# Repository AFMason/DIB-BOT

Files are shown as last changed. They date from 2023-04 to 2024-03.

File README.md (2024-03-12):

# DIB-BOT
Your guide to building and using DIB-BOT. This guide assumes you do not have a 3D printer already, and you've bought a new Ender3 for this project. If you've already got a 3D printer you can obviously skip some of these steps, or you might need to adapt. Good luck!
![Uploading 20230316_173502.jpg…]()

## Initial Setup
Step 1:
Acquire all the materials listed in "Shopping list.md"

Step 2:
Assemble the Ender 3. I found the method described by Chuck Hellebuyck (CHEPclub - Home, https://youtu.be/2Th2e7wTNV0) to be really useful. This differs slightly from the manufacturers instructions, and results in a more well-aligned printing bed. Of particular importance is to really tighten the belts - this improves the spatial resoltion of the printer and will help reduce positional variation of droplets between different wells.

Step 3: 
Do some test prints with the Ender3 to check if it has been assembled properly. You may need to tighten/align/troubleshoot before the Ender3 behaves reliably. For example the benchy boat, or CHEPs concentric circles.

Step 4: 
Print the nanoject holder (Nanoject_holder.stl, Nanoject_holder.gcode). I used PETG, you might be able to use another filament, if you don't use PETG you'll want to re-slice the .stl file as Nanoject_holder.gcode has been optimised for PETG. After printing, the bridge support and any small printing errors were carefully removed from the Nanoject holder with a scalpel and 120 grit sandpaper.

For DIB-BOT V1, you can stop here and start playing around with it. However, if you want to further automate the droplet deposition process and have the Ender3 control the Nanoject, you need to complete the following steps.

## Running DIB-BOT

### Developing a custom gcode print method

For this project I had to learn how to write gcode. This coding language has its roots in the first CNC metalworking machines from the 1950s, and is one of the first "high-level" programming languages. As such, its relatively simple to learn, particularly for the rudimentary cartesian movements that are performed by DIB-BOT. There are plenty of resources on Youtube, but I found websites like https://marlinfw.org/meta/gcode/ particularly useful for understanding specific commands (and Marlin is the "flavour" of gcode that the Ender3 runs on).  

I've annotated all of my code uploaded to this github, but below I've listed some of the most important commands:
```
G90 ;enable absolute positioning, so all movement commands are calculated relative to (0,0,0)
G91 ;enable relative positioning, so all movement commands are calculated relative to the current position
G28 ;Home all axes - this needs to happen at the start of every method to "zero" the axes

G1 X1 Y2 Z3 F3000 ; G1 is the basic move command. This particular line tells the printer to move to (1,2,3) in absolute positioning or move (+1,+2,+3) in relative positioning, at a speed of 3000 mm/min.
G4 S5 ;Pause for 5 seconds

M0 ;pause the print/method. The operator will need to press the resume button on the printer to continue the method. Useful for inserting indefinite pauses.
M0 Hello World ;Pauses the method and displays a little message, "Hello World" in this example. Useful for reminding the operator of what to do at every point, such as change the sample or check the tip calibration.

M104 S0 ;sets the hot end to 0 °C, to ensure nothing gets hot
M190 S0 ;sets the bed temperature to 0 °C
M107 ;turns the fan (FAN3) on the hot end OFF
M106 ;turns FAN3 ON
M300 P100 ;tells the 3D printer to emit a short beep from its internal speaker, length 100 ms in this example
```

**How to write/review/edit gcode**

You can use any plain text editor like Notepad. Just make sure you save it as a *.gcode file (for example, a file named "test print.gcode"), otherwise the Ender3 won't be able to read it.

I edit my gcode in Notepad++ (https://notepad-plus-plus.org/downloads/) using the custom language profile created by Eldar Gerfanov (https://zero-divide.net/?article_id=4809_notepad-absolutely-free-g-code-editor-with-code-highlighting) which just makes writing code a little bit cleaner and easier in my experience. If you're going to write a lot of gcode you'll be doing lots of find and replace actions which works well in Notepad ++.

### Importance of calibration

The 3D printer doesn't know where your 384-well plate is, how deep the wells are, or how long the pulled microcapillary is. At the start of all my gcode methods you'll find some calibration code:
```
G28 ; Home all axis
G1 Z150 F3000 ; Lift Z axis and load first solution
M106; fan on to open relay, enable fill/empty/inject button
M0 load dye; pause print, load first droplet solution
G1 X45.0 Y129.9 F3000
G1 Z68.3 
M0 check nozzle height
G1 Z70
G1 X51.1 Y162.4 F3000; Move to start - 1A - check position of plate
G4 S1
M300 P100 ; short beep
G4 S1
M300 P100
G4 S1
M300 P100
M0 check start position; Pause print, check plate alignment
```
The first G1 move lifts the print head to +150 mm, and then pauses. This is to provide plenty of clearance from the well plate, so the tip doesn't crash into it, and raises it to a nice ergonomic position to load the first aqueous solution. It then navigates to X45, Y129.9, Z68.3 before pausing again. Z68.3 was the exact position that was selected where the top of the well plate just touched the tip of the pulled capillary. It is important to mount the nanoinjector deliberately high in the harness, such that when you're at Z68.3, you need to lower the nanoinjector down a few millimeters manually to find the perfect "just touching" position. ***If you don't do this step you run the risk of crashing your tip into the plate during this first calibration step.*** 

Next, the print head will raise up to Z70 - 1.7 mm above the plate surface. This is the height that throughout the method is used to travel in x and y. It will then navigate to X51.1 Y162.4 and the pause again for you to check the xy calibration. If you're using the 3D printed well plate holder I have designed, and aligned it the left and bottom edges of the build plate, then the nozzle should be centered over well 1A. If its not centered, you have 2 options - move the well plate, or change the code. I do the latter, and use the manual movement controls on the printer itself to find the position of 1A, and then update the calibration code. ***This is vital to get correct, as the majority of the patterning gcode is executed in relative positioning (G91). So, if you don't nail the position of the first well, every other well won't work either***

### Materials

**1. Pulling capillaries to make nanoinjector nozzles** Micropipettes were pulled using a Sutter P-87 capillary puller. The puller was set in the following manner: heat = ramp (672), pull = 0, v = 40, time = 250, pressure = 500. The puller should loop twice, with the capillary breaking on the second loop. If the capillary snaps on the first loop, lower the heat and/or velocity parameters in small increments. Before mounting in the Nanoject, micropipettes were confidently but gently stabbed through a single sheet of kimwipe paper to break the tip cleanly, which was verified using a transmitted light microscope (4x objective). You can find a great resource for variations to this method in the "methods" folder, "capillary cookbook.pdf".

You can pull capillaries manually (as in heat up a capillary over a bunsen burner and pull) but this results in pretty rough nozzles. These instruments are regularly used in electrophysiology labs - if you're at a university, ask around. I didn't have one in my lab, but would pull batches of capillaries that last for a month or two. I have not yet found a good low-cost/open source capillary puller...

**2. Preparing lipid solutions** The "lipid-out" approach was employed, where lipids are dissolved in the oil phase. DPhPC was purchased from Sigma-Aldrich as a powder. The entire 200 mg vial was dissolved in chloroform to a concentration of 100 mg/ml. Aliquots of this stock solution were transferred to 2 mL glass HPLC vials and dried to a film under a stream of nitrogen. For example, 50 uL aliquots results in 10 mg per vial, perfect for redissolving with 1 mL of hexadecane to get 5 mg/mL. DPhPC films were further dried in vacuo for at least 18 hours before further use, and stored under nitrogen at -20 °C if not used immediately. 

**3. Preparing aqueous solutions** Full details can be found in the preprint, this depends on the experiment. Typically, aqueous solutions were buffered with 10 mM HEPES at pH 7, with approximately 1 M KCl.

### Running a custom gcode print method

**1. Load a pulled capillary** Remove the black plastic collet from the NanojectII and carefully remove the upper-most black O-ring from the stainless steel piston. You can do the following back-filling of the capillary in many different ways, but this worked best for me. The main thing is you want to fill the capillary with your oil phase without breaking the sharp end, and without introducing any air bubbles. First, I filled a 1 mL plastic syringe with hexadecane, and attached a blunt stainless steel 30g x 2" needle, gently depressing the plunger of the syringe to expel any air from the needle. Second, I placed the collect on the capillary before I pushed the black O-ring onto the blunt end of the pulled capillary and adjusted it to be 1-2 mm from the end (as this is where it will sit when it is inserted again in the Nanoject). I then back filled the pulled capillary, leaving a small amount to flow over the top of the blunt end. Using a kimwipe, I then gently blotted away any excess oil on the outside of the capillary and O-ring, but leaving the blunt aperture of the capillary with excess oil. Next, I carefully installed the capillary back onto the Nanoject, not tightening the collet too much. If there is any air in the capillary next to the stainless steel piston, do it again. Air bubbles are compressible and this can introduce issues with injection volume consistency, or failed injections (ie you press Inject and nothing comes out).

Once the capillary is back-filled with hexadecane, press "Empty" on the Nanoject control until the air is expelled from the sharp end. Mount the Nanoject in the 3D-printed harness on the x-stage of the Ender3, *taking care to mount the Nanoject high, so that when the next calibration step is carried out, you need to lower it. If you don't have it high enough, it may crash during the initialisation, breaking your tip. Pulled capillaries vary in length so this is impossible to fix for now. Finally, unless you have upgraded to v3 with automated sample loading, you can load your aqueous sample.
[insert image of correct loading height]

**2. Perform the calibration steps as outlined above**

**3. Droplet injection** With v1 of the DIB-BOT, there is no communication between the 3D printer and the Nanoject. In v1 methods, a pause is programmed when the nozzle is at the bottom of each well. The Ender3 will beep at you when its ready and thats your cue to press the "Inject" button on the Nanoject control box, and then push the knob in on the Ender3 to continue the method. I got pretty bored of this very quickly and modified the DIB-BOT to streamline this process, but it does work.

**4. Exchanging nozzle contents** If you want to have different aqueous contents on either side of the bilayer, you'll need to change the contents of your nozzle. In V1 methods, the following code facilitates this (was written for a 96 well plate with 9 mm centre-to-centre distance):
```
;change pipette contents
G1 Z80 ;lift pipette high
G1 Y-170 F3000 ;pushes plate back and out of the way
G4 S1
M25; pause to rinse +reload pipette
G1 Y161 F3000 ; brings plate
G1 Z-68; lower to travel position
M300 P100 ; short beep
G4 S2
M25 ; Pause print
```
After the nozzle has been raised up, carefully "Empty" the Nanoject, and then "Fill" with buffer or Milliq. Repeat this 2-3 times before filling with the next sample. It's tricky (which inspired v3 development) and you want to avoid touching the tip of the nozzle against the wall of the eppendorf tube, as this can cause imperceptible movement to the capillary and result in droplets not landing adjacent to the first droplet (thus failing to make a DIB). All the results from the paper were generated using v4 methods but you can still definitely make lots of good DIBs if you've got a steady hand with v1/v2.

## DIB-BOT v2: Automated droplet injection

Now you're ready to upgrade to v2 of DIB-BOT. This involves some hardware tinkering that may void your warranty on the Ender3 (as it involves opening up the motherboard case), and some additional elements in the gcode. The effort is worth it though, the result is a lot less button pushing.

### Modifications to DIB-BOT

1. You need to make a wire that connects the NanojectII to the Ender3. One end of this is a standard 3.5 mm 2-pole connector (same as you would find on  wired headphones). You can find this part easily online or at your local hobby/electronics store (I bought one from Jaycar here in Australia for less than $1). You'll need to solder the ends of the wire to the terminals inthe 3.5 mm connector, I don't think the polarity matters as the action of closing the circuit triggers the NanojectII, but you can follow my example which definitely works.
Artboard 1-100

2. The other end of this cable will connect to the [CON2] screw connectors on the relay module (also from Jaycar, Cat# XC4419, 5V relay, $7.95). As per the above circuit diagram, connect one wire to the "common" screw, and the other to the "NO" screw (stands for normally open, ie the resting state is an open circuit).


3. Then connect using female-female jumper leads the relay to the Ender3 motherboard, as per the circuit diagram above and photo below.


Orange wire from "S" (signal) on relay connects to negative terminal of FAN1
Red wire from "V" (supply voltage) on relay connects to Pin 2, denoted V, on the BLTouch header
Black wire from "G" (ground) on relay connects to Pin 1, denoted G, on the BLTouch header

### Modifications to gcode

-fan off/fan on cycling

-importance of delays

### Running DIB-BOTv2

## DIB-BOTv3: Semi-automated sample loading

The trickiest part of running DIB-BOTv2 is now sample exchange and rinsing the capillary - it is very easy to either break the tip of the capillary or nudge it so that its x/y position is out by 10s of microns, potentially decreasing your DIB yield. With DIB-BOTv3, the operator no longer has to hold a small tube up to the capillary; instead the capillary translates to one of 3 eppendorf tube holders in the plate holder to either dump to waste, fill with clean buffer/water, or load new sample.

### Modifications to gcode

### Running DIB-BOTv3

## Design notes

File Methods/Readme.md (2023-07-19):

In this folder you'll find a selection of the most recent gcode method files I have written. They have been written for a specific experiment which is described in detail in the soon to be released manuscript. In the sub-folder "Historical methods" you can find earlier, less refined methods, to document the progression of the DIB-BOT.

In each gcode files I have annotated each line that matters, to explain what that line of code does to the printer. This should hopefully allow you to make adjustments easily.

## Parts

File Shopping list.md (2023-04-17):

Everything you need to build the DIB-BOT. For materials needed to conduct experiments, check out the paper.
 
1. PETG filament (https://www.inkstation.com.au/2102/petg-3d-filament-175mm-silver-1kg-roll-p-18777.html?queryID=29b280d231a7040a4940cce4f01be405&objectID=18591#18591)
2. Dongle single channel 5 V relay (https://www.jaycar.com.au/duinotech-arduino-compatible-5v-relay/p/XC4419?pos=1&queryId=fd5d4861d8dd5a5220dddf146e065b07&sort=relevance&searchText=relay%20arduino) 
3. Jumper cables (https://www.jaycar.com.au/jumper-lead-mixed-pack-100-pieces/p/WC6027?pos=2&queryId=66a482975f8ff08bda1e47b8542ebf3a)
4. 3.5 mm stereo jack (https://www.jaycar.com.au/3-5mm-miniature-plug-black/p/PP0114?pos=4&queryId=0c1a85f003a799f6b1739a12a0a1efc3&sort=3.relevance)
5. Drummon glass capillaries, 3.5" (https://www.drummondsci.com/product/microinjection/glass-capillaries-for-all-nanoject-models-100-vl/?attribute_pa_height=3-5-inches)
6.

Equipment

1. Creality Ender3 (https://www.inkstation.com.au/2573/creality-ender-3-3d-printer-with-resume-printing-p-18159.html?16944&msclkid=799c40943ef71faff69624a8fb18bed5&utm_source=bing&utm_medium=cpc&utm_campaign=Smart%20Shopping%20Campaign%20(Cable)&utm_term=4580153138567049&utm_content=Ad%20group%20%231) 
2. Drummond Nanoject II (https://www.drummondsci.com/product/microinjection/nanoject-ii-auto-nanoliter-injector/)
3. Soldering iron
4. Wire strippers 
5.

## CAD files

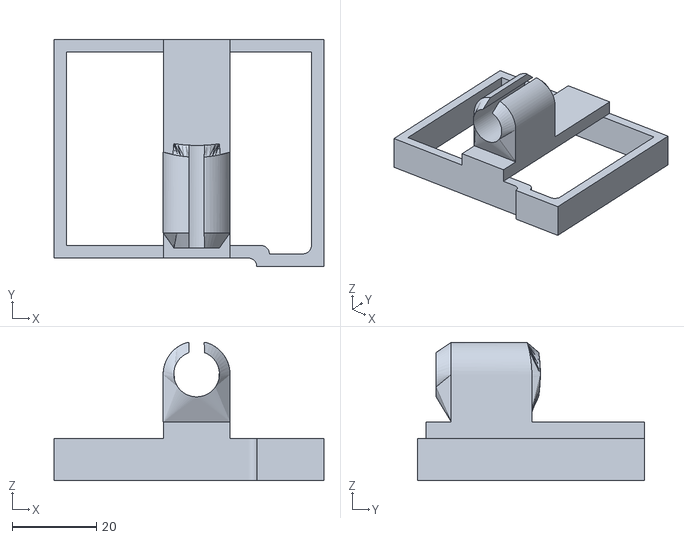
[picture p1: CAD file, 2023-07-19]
Setup/nanoinject holder_rough.stl
64.2 x 54.0 x 32.9

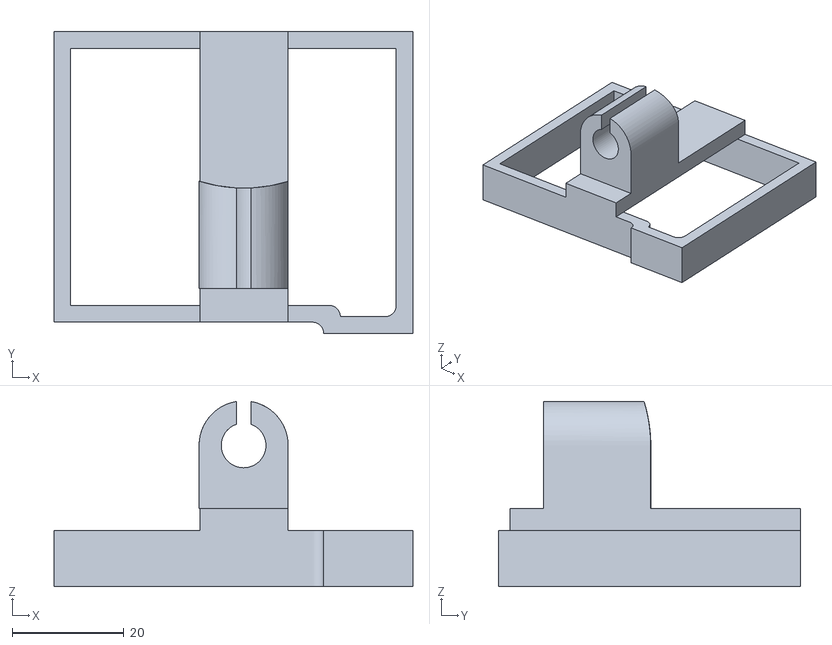
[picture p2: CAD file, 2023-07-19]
Setup/dial_indicator_holder_v2.stl
64.2 x 54.0 x 33.1

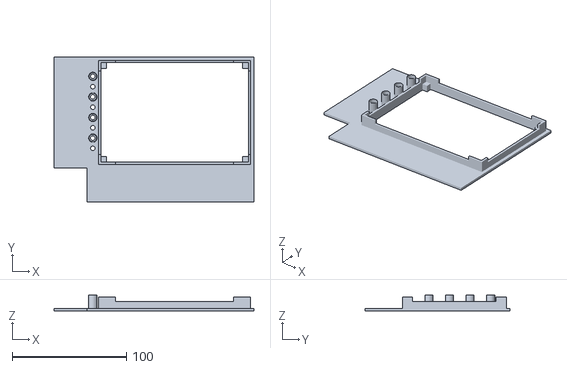
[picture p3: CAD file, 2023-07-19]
Setup/96-well with skirt_v2.stl
175.0 x 127.0 x 14.0

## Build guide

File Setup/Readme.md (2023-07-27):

  In this folder you'll find all the requisite *.stl models for the bits and pieces you need to make the DIB-BOT, photos of the build, and anything else I think of that might be useful.
![Uploading 20230316_173502.jpg…]()

![Uploading 20230209_114219.jpg…]()
